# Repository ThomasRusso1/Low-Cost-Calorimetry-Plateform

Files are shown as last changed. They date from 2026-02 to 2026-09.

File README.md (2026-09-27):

# Low-Cost-Calorimetry-Plateform
This repository introduces the low-cost calorimetry platform I have developed at the University of Minho (Portugal) in the framework of my PhD thesis. This platform allows to conduct isothermal and adiabatic calorimetry with lab-grade accuracy, as well as DSC applications. Each of the calorimetry modes can be seen as a module; the electronic hardware and software is the same for all applications. The extensive validation process can be found in my thesis, which I will refer to once published.
The calorimetric cells allowing for heat flux monitoring for isothermal and DSC applications have been made from off-the-shelf components easily available at regular hardware and electronic stores. The adiabatic module is represented by a modified soil permeability test mould; however, water-tight container with cable-pass and an internal volume of around 2L can do the job.
The description of the BoM, CAD parts, Assembly, and different codes required can be found in the various files of this repository.


## How to proceed:
1. **Get the components:** Get the different components, which you can find in [click for BoM](Hardware/BoM.csv)
2. **3D print the needed parts:** Print the different parts you need: [calorimetric cell](Hardware/Calorimetric_cell.stp) ; [carter base](Hardware/carter_part1.stp) ; [carter top](Hardware/carter_part2.stp) ; [Specimen mould](Specimen_mould.stp)
3. **Electronic assembly:** Assemble and connect the electronic components as in the diagram presented in [click for interaction diagram](Hardware/images/Components_interaction_diagram.png). Connect the Peltier cells to the Linduino. 
4. **Create your calorimetric cells:** Follow the steps from [click for assembly steps](Hardware/Calorimetric_cells_assembly_steps.md) to create your calorimetric cells.
5. **Adiabatic module:** Find or make the adequate water-tight container to create your adiabatic module, like in [click for adiabatic module](Hardware/images/Adiabatic_module_pictures.png)
6. **Upload Arduino code:** Upload the code to your arduino [click for Arduino code](Software/Arduino_code)
7. **Upload Linduino code:** Upload the Linduino code so it can record temperature and Peltier cells data and communicate with the Arduino [click for Linduino code](Software/Linduino_code)
8. **Setup your Python App:** Setup the Python app in the Raspberry Pi for GUI and data storage [click for Python app](Software/Python_App)
9. **Enjoy your lab-grade calorimetry platform!** Enjoy, don't hesitate to contribute and if you have any question feel free to ask. The software in this repository is licensed under the MIT License. The hardware designs are licensed under the CERN-OHL-P. See the respective LICENSE files for details.

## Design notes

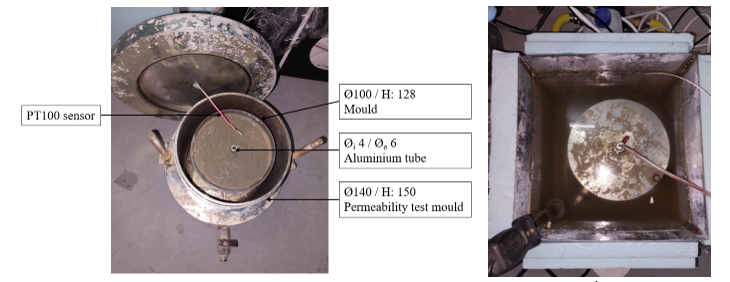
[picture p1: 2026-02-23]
Hardware/images/Adiabatic_module_pictures.png

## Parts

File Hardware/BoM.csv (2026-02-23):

Component | Quantity
Water bath | 1
Water pump | 1
Set of hoses and connections for pump | 1
Water heater | 1
Arduino Mega | 1
PT100 sensors | 2
LCD screen | 1
Solid state relays (AC) | 2
Raspberry Pi | 1
SD card | 1
Analog devices DC2420-A KIT | 1
precision resistor 120 Ohm | 1
Peltier cells (12V4A) | 2
Digital isolator | 1

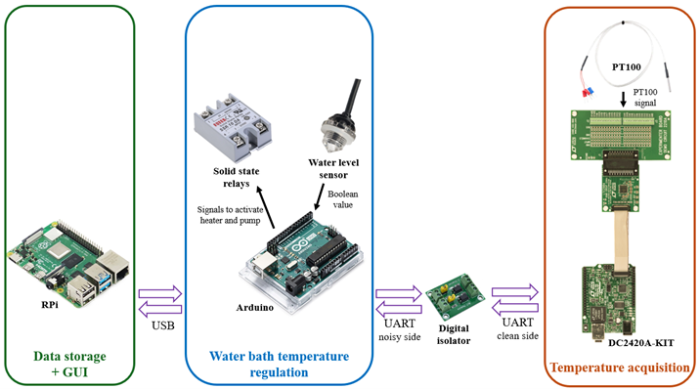
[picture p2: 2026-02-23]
Hardware/images/Components_interaction_diagram.png

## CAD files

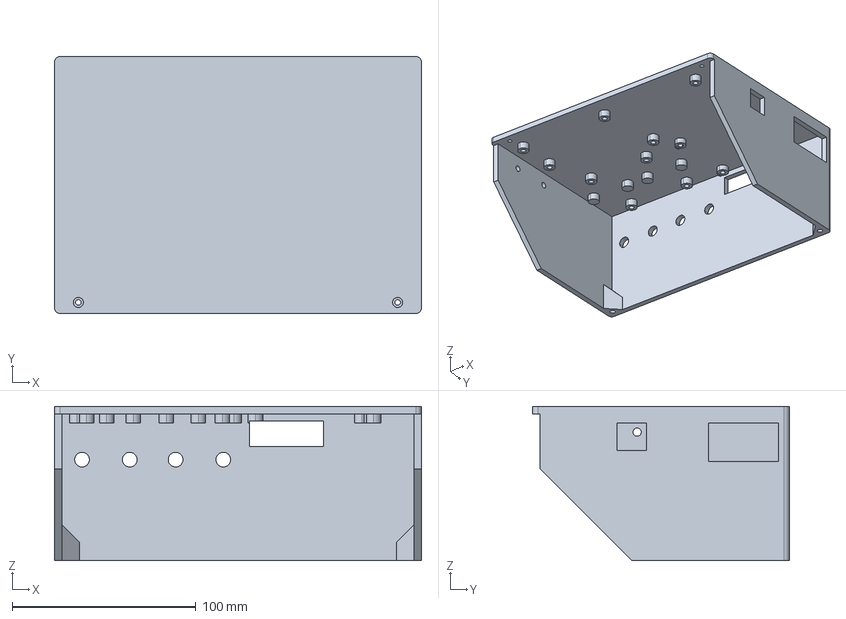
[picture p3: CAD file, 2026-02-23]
Hardware/carter_part1.stp
200.0 x 140.0 x 84.0 mm

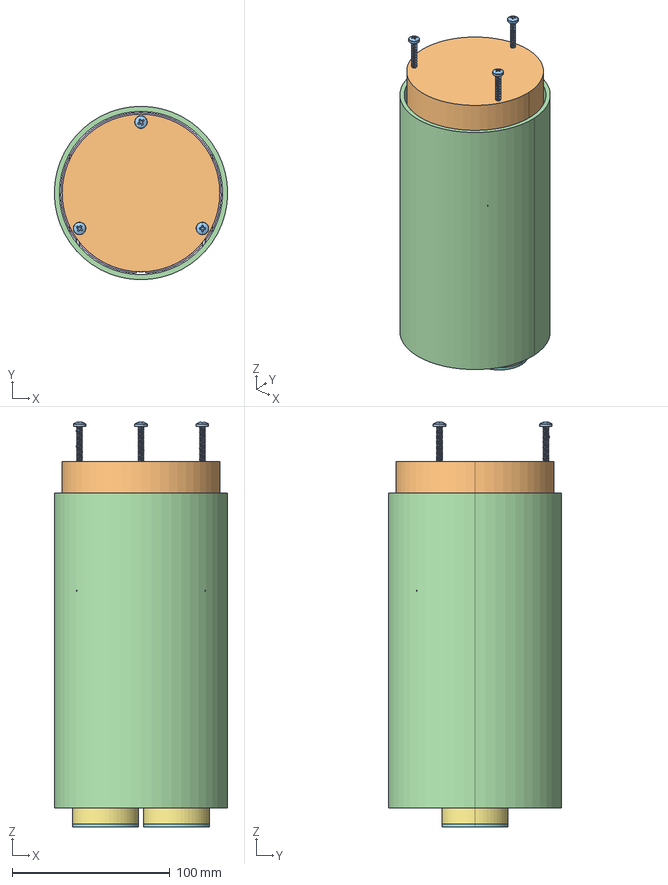
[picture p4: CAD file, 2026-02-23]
Hardware/Calorimetric_cell.stp
110.0 x 110.0 x 257.0 mm
STEEL_BLOCK
PELTIER_ELEMENT_40X40MM_TEC1-12_ASM x 2
PANHEADCROSSRECESSEDSCREW_M4X30 x 3
TUBE_PVC_110
SHELL_FOAM_FILLING
SHELL_LEAD
REACTOR_LEAD x 2
REATOR_LEAD_OF_LEAD x 2
MOULD_ADAPTED_V3 x 2
MOULD_LEAD_V3 x 2

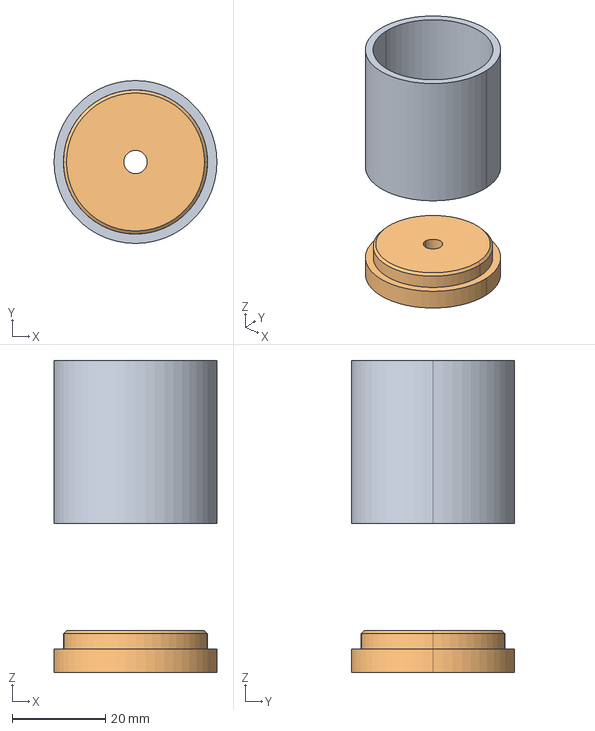
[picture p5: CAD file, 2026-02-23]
Hardware/Specimen_mould.stp
35.0 x 35.0 x 67.0 mm
MOULD_ADAPTED_V3
MOULD_LEAD_V3

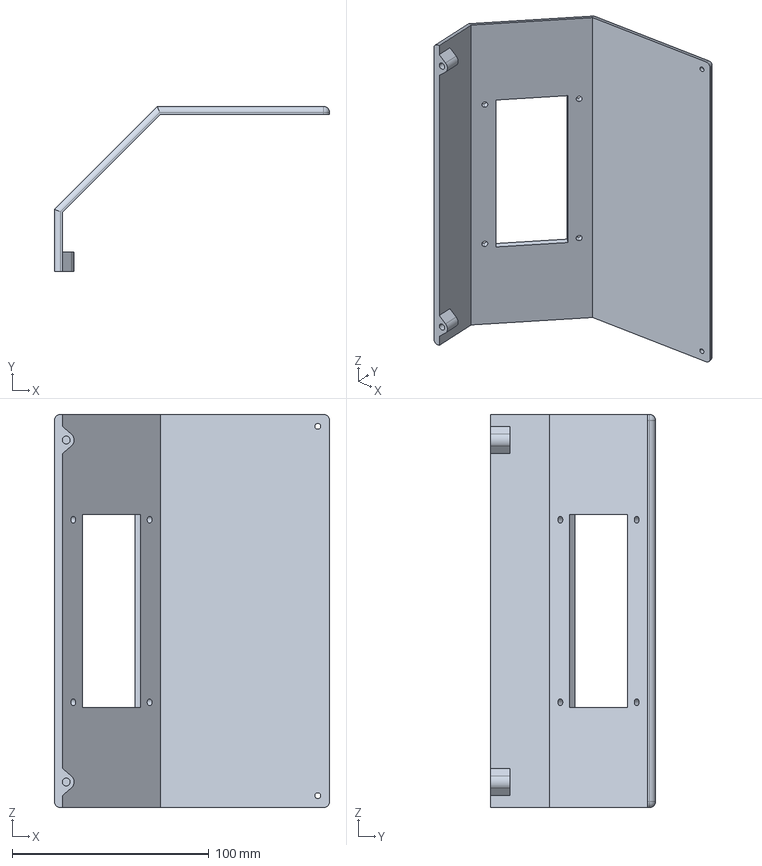
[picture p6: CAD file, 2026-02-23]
Hardware/carter_part2.stp
140.0 x 84.0 x 200.0 mm

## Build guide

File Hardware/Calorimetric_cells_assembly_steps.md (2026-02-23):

Assembling the calorimetric cells is quite straight forward once you have all the components: Peltier cells, aluminium bloc (heat sink), thermal conductive paste, 3D printed channels separator and PVC tube.
### Assembly steps:

1. **Place Peltier cells:** First, place the Peltier cells onto the aluminium block with thermal conductive paste at the interface between the aluminium and peltier cells.
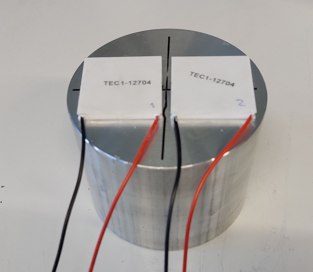
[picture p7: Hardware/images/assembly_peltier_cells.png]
peltier cells assembly


2. **Channels separator:** Then, place the channels separator; you can hot glue it to the aluminium block to ensure it won't move.
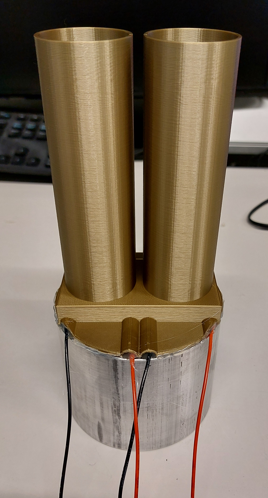
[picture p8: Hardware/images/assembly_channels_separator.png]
separator placement


3. **PVC tube:** After that, place the PVC tube and pass the cables out from the top of the PVC tube.
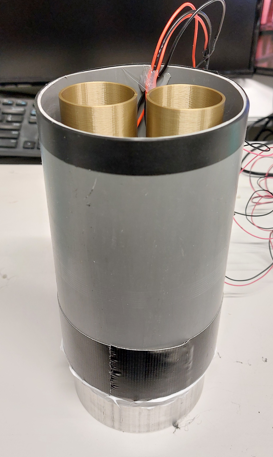
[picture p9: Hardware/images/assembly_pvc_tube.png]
PVC tube


4. **Water tightness:** Now the cell needs to be water-tight from under; for that, place tightning collars around the PVC tube to firmly clamp it to the block; you can then tape the PVC tube to the aluminium block to create a temporary water-tight-ish assembly. Then poor liquide silicone in the small gap between the tube and block; when it hardens it will be fully water-tight.
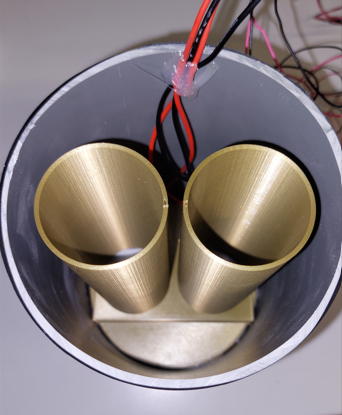
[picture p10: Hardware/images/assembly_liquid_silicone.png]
liquid silicone


5. **Isolating foam:** You can now spray isolating foam all around the PVC tube and channels separator. Choose a foam adapted for moist environments.
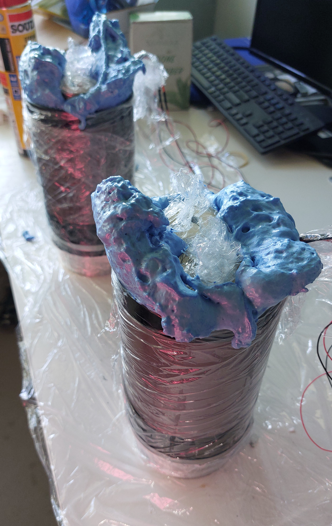
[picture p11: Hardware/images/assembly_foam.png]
spray foam


6. **Foam cutting:** Once the foam has hardened, you can cut the exceedent, revealing your calorimetric channels.
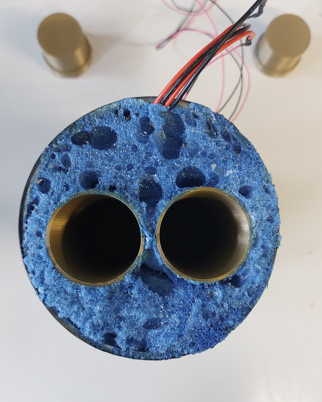
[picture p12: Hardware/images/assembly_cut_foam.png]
cut foam


7. **Lids preparation:** Do the same procedure for the channel lids.
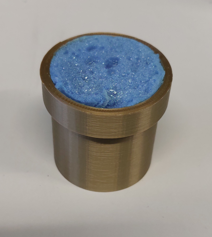
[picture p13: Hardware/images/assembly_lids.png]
lids


8. **Congrats:** Enjoy your DIY-made calorimetric cell! Congrats!
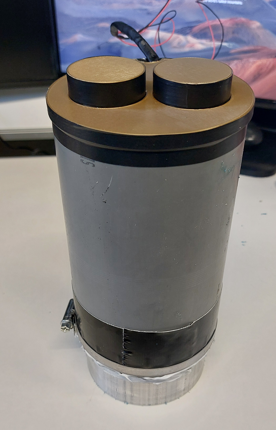
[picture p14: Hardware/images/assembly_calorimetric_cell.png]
cells
 
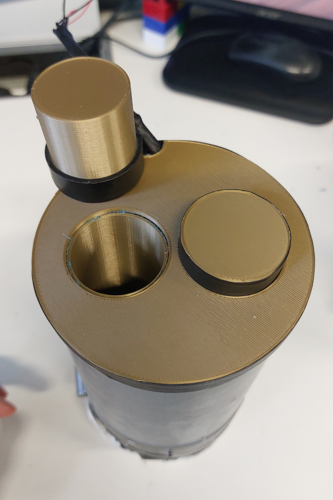
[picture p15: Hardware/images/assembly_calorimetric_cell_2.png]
cells_2


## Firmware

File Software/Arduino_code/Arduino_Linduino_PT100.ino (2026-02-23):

#include <Adafruit_MAX31865.h>
#include <LiquidCrystal_I2C.h>
#include <PID_v1.h>

// --- Pin Definitions & Constants ---
#define HEATER_RELAY_PIN 13
#define POT_RELAY_PIN 8
#define RREF 4300.0      // For PT1000 with a 4.3k Ohm reference resistor
#define RNOMINAL 1000.0  // For a PT1000 sensor

// --- System Objects ---
Adafruit_MAX31865 local_rtd = Adafruit_MAX31865(3);  // Local RTD for absolute water temp
LiquidCrystal_I2C lcd(0x27, 20, 4);

// --- PID Configuration ---
double Setpoint, Input, Output;
double Kp = 18, Ki = 5, Kd = 8;
PID myPID(&Input, &Output, &Setpoint, Kp, Ki, Kd, P_ON_M, DIRECT);
int windowSize = 2000;
unsigned long windowStartTime;

// --- Temperature & State Variables ---
float tempWater_RTD = 0.0;      // Absolute temperature from the local RTD sensor
float tc_temp_water = 0.0;      // Temperature from the water thermocouple (from Linduino)
float tc_temp_mortar = 0.0;     // Temperature from the mortar thermocouple (from Linduino)
// Variables for Water Sensor
const int SAMPLE_COUNT = 30;  // Number of samples to average
float tempHistory_water[SAMPLE_COUNT];
float total_water = 0.0;
int currentIndex_water = 0;


// --- System Mode Flags ---
bool is_running = true;
bool was_running = true;
bool matchingMode = false;
bool calibrationMode = false;
bool rampTest = false;
double gap = 0.0;
unsigned long lastLinduinoMessageTime = 0;
bool LinduinoConnection = true;
bool rampingUp = true;

const int final_setpoint = 70;
const int final_setpoint_ramp = 26;
// Timing variables
unsigned long currentTime, previousTime, startTime;
double elapsedTime;  // For measuring time elapsed in seconds
unsigned long setpointCheck;

float Peltier_cell_1;
float Peltier_cell_2;

// =================================================================
//  FORWARD DECLARATIONS
// =================================================================
void read_sensors();
void process_commands();
void update_pid_and_setpoint();
void control_heater();
void update_display();
float get_corrected_thermocouple_temp(float raw_tc_temp);
int find_closest_index(int value_to_find);
int heat=0;

// =================================================================
//  SETUP
// =================================================================
void setup() {
  Serial.begin(9600);   // To PC / RPi
  Serial1.begin(9600);  // To Linduino

  pinMode(HEATER_RELAY_PIN, OUTPUT);
  pinMode(POT_RELAY_PIN, OUTPUT);

  lcd.init();
  lcd.backlight();
  lcd.print("System Starting...");

  local_rtd.begin(MAX31865_3WIRE);
  float initial_temp_water = local_rtd.temperature(RNOMINAL, RREF);
  for (int i = 0; i < SAMPLE_COUNT; i++) {
    tempHistory_water[i] = initial_temp_water;
    total_water += initial_temp_water;
  }
  tempWater_RTD = total_water / SAMPLE_COUNT;

  myPID.SetOutputLimits(100, windowSize);
  myPID.SetMode(AUTOMATIC);

  Input = 20.0;
  Setpoint = 18.0;

  windowStartTime = millis();
  delay(1500);
  lcd.clear();
}

// =================================================================
//  MAIN LOOP
// =================================================================
void loop() {
  unsigned long currentTime = millis();
  elapsedTime = (currentTime - startTime) / 1000.0;
  read_sensors();
  process_commands();

  if (is_running) {
    update_pid_and_setpoint();
    control_heater();
    digitalWrite(POT_RELAY_PIN, HIGH);
  } else {
    digitalWrite(HEATER_RELAY_PIN, LOW);
    digitalWrite(POT_RELAY_PIN, LOW);
  }

  update_display();
  delay(100);
}

// =================================================================
//  HELPER FUNCTIONS
// =================================================================

/**
 * Reads data from the local RTD sensor and from the Linduino.
 */
void read_sensors() {
  // --- Update Water Sensor Reading (same logic) ---
  total_water = total_water - tempHistory_water[currentIndex_water];
  tempHistory_water[currentIndex_water] = local_rtd.temperature(RNOMINAL, RREF);
  total_water = total_water + tempHistory_water[currentIndex_water];
  tempWater_RTD = total_water / SAMPLE_COUNT;
  currentIndex_water++;
  if (currentIndex_water >= SAMPLE_COUNT) {
    currentIndex_water = 0;
  }
  if (Serial1.available() > 0) {
    lastLinduinoMessageTime = millis();
    String dataFromLinduino = Serial1.readStringUntil('\n');
    
    // Debugging: Uncomment the line below to see exactly what arrives
    // Serial.print("RAW DATA: "); Serial.println(dataFromLinduino);
    // Find all three commas
    int comma1 = dataFromLinduino.indexOf(',');
    int comma2 = dataFromLinduino.indexOf(',', comma1 + 1);
    int comma3 = dataFromLinduino.indexOf(',', comma2 + 1);
    // Ensure we found all 3 commas before parsing
    if (comma1 > 0 && comma2 > 0 && comma3 > 0) {
        // 1. Water Temp (Start to 1st comma)
        tc_temp_water = dataFromLinduino.substring(0, comma1).toFloat();
              // 2. Mortar Temp (Between 1st and 2nd comma)
        tc_temp_mortar = dataFromLinduino.substring(comma1 + 1, comma2).toFloat();
              // 3. Peltier 1 (Between 2nd and 3rd comma)
        Peltier_cell_1 = dataFromLinduino.substring(comma2 + 1, comma3).toFloat();
        // 4. Peltier 2 (After 3rd comma to end)
        Peltier_cell_2 = dataFromLinduino.substring(comma3 + 1).toFloat();
    }
  }
}

/**
 * Checks for commands from the PC/RPi and updates the system mode.
 */
void process_commands() {
  // This function is where you will place your logic for reading commands
  // from the PC to change modes (e.g., switch to matchingMode).
  // Example:
  if (Serial.available()) {
    String command = Serial.readStringUntil('\n');
    if (command.startsWith("R")) {
      Serial.print(tc_temp_mortar);
      Serial.print(",");
      Serial.print(tc_temp_water);
      Serial.print(",");
      Serial.print(Setpoint);
      Serial.print(",");
      Serial.print(tempWater_RTD);
      Serial.print(",");
      Serial.print(Peltier_cell_1,6);
      Serial.print(",");
      Serial.println(Peltier_cell_2,6);
    } else if (command.startsWith("S")) {
      matchingMode = false;
      calibrationMode = false;
      rampTest = false;
      is_running = true;         // Re-enable the process
      LinduinoConnection = true; // Reset the connection status for the new run
      Setpoint = command.substring(1).toFloat();
    } else if (command.startsWith("M")) {
      matchingMode = true;
      rampTest = false;
      calibrationMode = false;
      is_running = true;         // Re-enable the process
      LinduinoConnection = true; // Reset the connection status for the new run
      gap = command.substring(1).toFloat();
    } else if (command.startsWith("C")) {
      matchingMode = false;
      rampTest = false;
      calibrationMode = true;
      Setpoint = 24.5;
      is_running = true;         // Re-enable the process
      LinduinoConnection = true; // Reset the connection status for the new run
    } else if (command.startsWith("P")) {
      matchingMode = false;
      calibrationMode = false;
      rampTest = true;
      rampingUp = true;
      Setpoint = 18;
      setpointCheck = elapsedTime;
      is_running = true;         // Re-enable the process
      LinduinoConnection = true; // Reset the connection status for the new run
    }
  }
}
/**
 * Sets the PID Input and Setpoint based on the current operational mode.
 */
void update_pid_and_setpoint() {
  // --- SAFETY CHECK ---
  if (millis() - lastLinduinoMessageTime > 10000) { // 10-second timeout
    is_running = false;
    LinduinoConnection = false;
    digitalWrite(HEATER_RELAY_PIN, LOW);
    digitalWrite(POT_RELAY_PIN, LOW);
    return;
  }
  // --- In Matching Mode, use the differential thermocouple system with RTD-based correction ---
  if (matchingMode) {
    //Avec les PT100, on voit que Tw-Tm=0.12
    const float m = 0;
    const float c = 0.12;
    const float safety = 0.03;
    float tc_offset = (m * tc_temp_water) + c;
    Input = tc_temp_water;
    Setpoint = tc_temp_mortar + tc_offset - safety;

  } else {
    // --- In all OTHER modes (Static, Calibration, Ramp), use the local absolute RTD system ---
    // The PID Input is the absolute temperature of the water from the local RTD.
    Input = tc_temp_water;
  }
  // The Setpoint is determined by the logic for these other modes
  // (e.g., a fixed value from an 'S' command, or a ramping value).
  if (calibrationMode) {
    if ((elapsedTime - setpointCheck) >= 600) {
      Setpoint += 0.5;
      setpointCheck = elapsedTime;
    }
    if (Setpoint > final_setpoint) {
      is_running=false;
    }
    // Add your setpoint ramping logic for calibration here
  } else if (rampTest) {
    // Check if 2 hours (7200 seconds) have passed
    // Note: 3600 * 2 = 7200 seconds
    if ((elapsedTime - setpointCheck) >= 21600) {
      
      setpointCheck = elapsedTime; // Reset timer for the next 2-hour wait

      if (rampingUp) {
        // --- LOGIC FOR RAMPING UP ---
        
        // Only increase if we haven't reached the top yet
        if (Setpoint < final_setpoint_ramp) {
           Setpoint += 1; 
        }

        // Check if we have reached the peak (30 degrees)
        // We use >= to handle potential small floating point differences
        if (Setpoint >= final_setpoint_ramp) {
          rampingUp = false; // Switch direction! Next step will be down.
        }
      } 
      else {
        // --- LOGIC FOR RAMPING DOWN ---
        Setpoint -= 1;

        // Check if we have reached the bottom (25 degrees)
        if (Setpoint <= 17.0) {
          is_running = false; // Stop the test
        }
      }
    }
  }
}

/**
 * Runs the PID computation and controls the heater relay.
 */
void control_heater() {
  unsigned long now = millis();
  myPID.Compute();

  if (now - windowStartTime > windowSize) {
    windowStartTime += windowSize;
  }

  if (Output < (now - windowStartTime)) {
    digitalWrite(HEATER_RELAY_PIN, LOW);
    heat = 0;
  } else if (Input < Setpoint) {
    digitalWrite(HEATER_RELAY_PIN, HIGH);
    heat = 1;
  }
}

/**
 * Updates all information on the LCD screen.
 */
void update_display() {
  if (is_running){
    lcd.setCursor(0, 0);
    lcd.print("RTD: ");
    lcd.print(tempWater_RTD, 2);
    lcd.print("  ");
    lcd.print("H: ");
    lcd.print(heat);

    lcd.setCursor(0, 1);
    lcd.print("M: ");
    lcd.print(tc_temp_mortar, 2);
    lcd.print(" W: ");
    lcd.print(tc_temp_water, 2);
    lcd.print("   ");

    lcd.setCursor(0, 2);
    lcd.print("Targ:");
    lcd.print(Setpoint, 2);
    lcd.print(" In: ");
    lcd.print(Input, 2);

    lcd.setCursor(0, 3);
    lcd.print(" P:");
    lcd.print((Output / windowSize) * 100, 0);
    lcd.print("%     ");
  }
  else {
    if (was_running){
      if (LinduinoConnection) {
        lcd.clear();
        lcd.print("TEST FINISHED"); 
      }
      else {
        lcd.clear();
        lcd.print("Linduino Link LOST!");
      }
    }
  }
  was_running = is_running;
}

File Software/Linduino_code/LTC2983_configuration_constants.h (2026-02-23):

/*!



LTC2983_configuration_constants.h:
The configuration constants used to configure the LTC2983.


http://www.analog.com/en/products/analog-to-digital-converters/integrated-special-purpose-converters/digital-temperature-sensors/LTC2983.html

http://www.analog.com/en/products/analog-to-digital-converters/integrated-special-purpose-converters/digital-temperature-sensors/LTC2983#product-evaluationkit

$Revision: 1.11.5 $
$Date: April 5, 2021 $
Copyright (c) 2018, Analog Devices, Inc. (ADI)
All rights reserved.

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
1. Redistributions of source code must retain the above copyright notice, this
   list of conditions and the following disclaimer.
2. Redistributions in binary form must reproduce the above copyright notice,
   this list of conditions and the following disclaimer in the documentation
   and/or other materials provided with the distribution.

THIS SOFTWARE IS PROVIDED BY THE COPYRIGHT HOLDERS AND CONTRIBUTORS "AS IS" AND
ANY EXPRESS OR IMPLIED WARRANTIES, INCLUDING, BUT NOT LIMITED TO, THE IMPLIED
WARRANTIES OF MERCHANTABILITY AND FITNESS FOR A PARTICULAR PURPOSE ARE
DISCLAIMED. IN NO EVENT SHALL THE COPYRIGHT OWNER OR CONTRIBUTORS BE LIABLE FOR
ANY DIRECT, INDIRECT, INCIDENTAL, SPECIAL, EXEMPLARY, OR CONSEQUENTIAL DAMAGES
(INCLUDING, BUT NOT LIMITED TO, PROCUREMENT OF SUBSTITUTE GOODS OR SERVICES;
LOSS OF USE, DATA, OR PROFITS; OR BUSINESS INTERRUPTION) HOWEVER CAUSED AND
ON ANY THEORY OF LIABILITY, WHETHER IN CONTRACT, STRICT LIABILITY, OR TORT
(INCLUDING NEGLIGENCE OR OTHERWISE) ARISING IN ANY WAY OUT OF THE USE OF THIS
SOFTWARE, EVEN IF ADVISED OF THE POSSIBILITY OF SUCH DAMAGE.

The views and conclusions contained in the software and documentation are those
of the authors and should not be interpreted as representing official policies,
either expressed or implied, of Analog Devices, Inc.

The Analog Devices Linduino is not affiliated with the official Arduino team.
However, the Linduino is only possible because of the Arduino team's commitment
to the open-source community.  Please, visit http://www.arduino.cc and
http://store.arduino.cc , and consider a purchase that will help fund their
ongoing work.
*/
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

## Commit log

2026-02-23 updated bom
    [BoM.csv]
2026-02-23 Create Calorimetric cells assembly steps
2026-02-23 assembly pics added
2026-02-23 Update Calorimetric cells assembly steps
2026-02-23 Rename Calorimetric cells assembly steps to Calorimetric cells assembly steps.md
2026-02-23 Update Calorimetric cells assembly steps.md
2026-02-23 Rename Calorimetric cells assembly steps.md to Calorimetric_cells_assembly_steps.md
2026-02-23 updated names
    [Calorimetric_cell.stp, Specimen_mould.stp]
